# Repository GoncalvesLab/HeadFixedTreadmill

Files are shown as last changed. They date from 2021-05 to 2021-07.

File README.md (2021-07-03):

# HeadFixedTreadmill
This repository contains desgins to build a head-fixed linear treadmill apparatus and to run related data analysis.

Treadmill setups are a popular approach for in vivo recordings that require head-fixation and have been used by several labs
for example: Royer et al. 2012, Bittner et al. 2015, Danielson et al. 2016. This repository contains designs of custom-machined parts 
for a simple treadmill and head-fixation apparatus, as well as Arduino and Matlab code for tracking the position of the mouse and administer rewards.

Assembly:

Grounding of animal for lick detection: We implant a gold ground pin soldered to about 1 mm of tungsten wire above the cerebellum.
 
To assemble, clamp gold pin in a helping hand alligator clamp. Insert tungsten wire into the shallow hole of the flat end of the pin. Solder and then slip the wire approximately 1 mm from the pin. Likewise, solder a female connector to a long piece of wire (long enough to connect the mouse’s implanted pin to the lick counter) to ground the mouse. Solder a wire to the lick spout and connect it to the appropriate port on the lick counter. Licks will be sensed when a grounded mouse contacts the lick port, closing the circuit.

We tape the RFID scanner to the bottom of the mouse platform. Upload the RFID interface code to the Arduino Uno. Connect the RFID to the Arduino Uno, connect the following pins with jumper cables:

[RF522 Pin	->    Arduino Uno Pin (Digital)]

SDA	 ->         10

SCK	 ->         13

MOSI	->        11

MISO	->        12

IRQ	  ->        Not Used

GND	  ->        GND

RST	  ->        9

3.3 V	->        3.3V

To connect the Arduino Uno to the NI breakout box, solder jumper cables so that they have a split in one end. In other ones, one end of the cable will have a single tip (plugged into Arduino), and the other will have two tips (plugged into NI breakout box). This will give use two copies of the RFID signals: one is recorded and used for data analysis and the other is used as input to the pump. Connect the following pins with jumper cables:

[Arduino Uno Pin (Digital) ->	NI Breakout Box (Digital)]

2	-> P0-6 and PFI-5

3 -> P0-5 and PFI-4

4	-> P0-4 and PFI-3

5	-> P0-3 and PFI-2

6 -> P0-2 and PFI-1

Upload the rotary encoder interface code to the Arduino Due. To connect the rotary encoder to the Arduino Due, connect the following pins with jumper cables:

[Encoder Pins ->	Arduino Due Pins (Digital)]

Pin 1 (GND) ->	GND

Pin 2 	-> Not used

Pin 3 (Chan A) ->	3

Pin 4 (Vcc)	-> 5V

Pin 5 (Chan B) ->	4

To connect the Arduino Due to the NI breakout box, connect the DAC1 pin and a GND pin on the Due to a BNC adapter cable (DAC1 to voltage and GND to GND). Connect the BNC adapter to a BNC analog input on the NI breakout box (we use port analog input 0, or AI0).

To connect the lick counter to the breakout box, plug a BNC adapter cable into the lick counter output. Plus the voltage line into the port0/line7 on the NI breakout box and the GND into one of the digital GND ports.

For the pump command, we use a BNC splitter to send the output to the water pump for reward administration as well as to an input on the NI breakout box to record the command. To connect the NI breakout box to the water pump, plug a BNC adapter into digital port 0/line 0 and GND. Plug the adapter into a splitter. Use a BNC cable to plug one line into analog input 1 (AI1) and use a BNC adapter to plug the other line into the pump. For this, plug the voltage line into pin 2 on the pump's serial port and the GND into pin 9 of the pump's serial port.
 
Make sure jumper cables are stably connected. We happened to have old jumper cables whose pins fit perfectly into the pump TTL port, but many jumper cables fell out too easily to be used.

Acknowledgements:

The rotary encoder interface that tracks the velocity of the mouse is based on code by Steven Sawtelle (Janelia Research Campus).
The head-fixation bar was adapted from designs by the Golshani and Aharoni labs (UCLA).
The data acquisition routines in Matlab were adapted from code written by the Sjulson and Batista-Brito Labs (Einstein). We thank
Ehsan Sabri, Eliezyer Fermino De Oliveira, Luke Sjulson and Renata Batista-Brito for their technical advice and assistance.

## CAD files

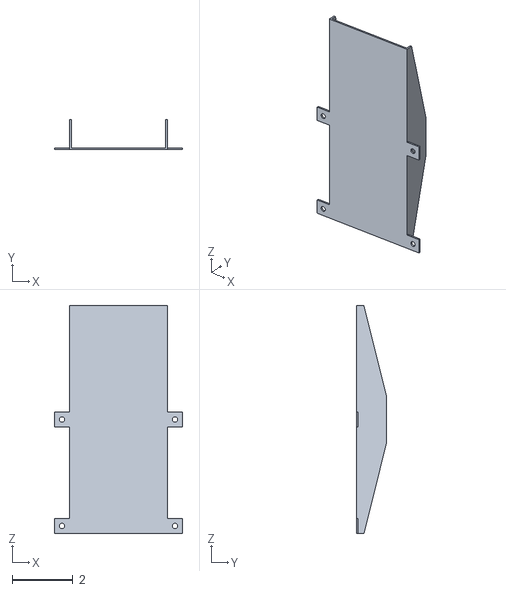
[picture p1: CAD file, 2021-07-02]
MousePlatform.stl
4.22 x 1.00 x 7.50

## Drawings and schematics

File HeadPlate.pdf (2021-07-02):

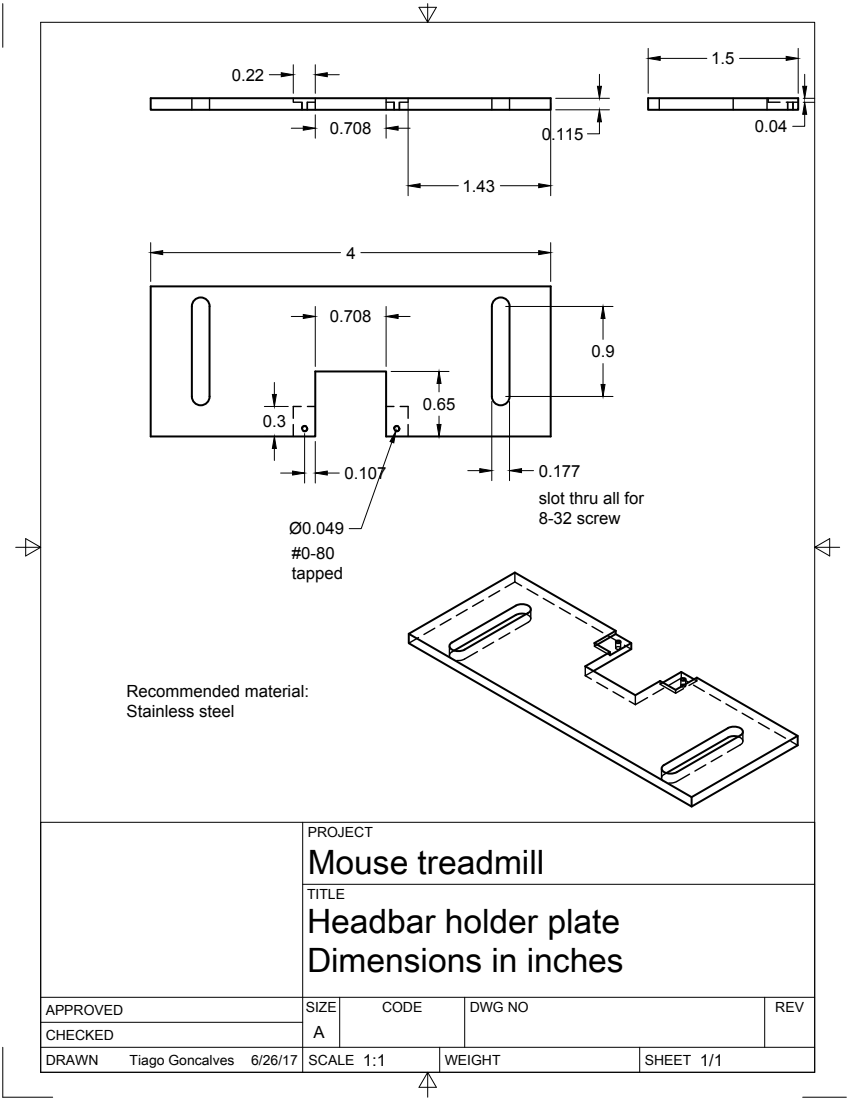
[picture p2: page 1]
SIZE; CODE; DWG NO; REV; Tiago Goncalves; Recommended material: Stainless steel

slot thru all for
8-32 screw

PROJECT
Mouse treadmill
Headbar holder plate
Dimensions in inches

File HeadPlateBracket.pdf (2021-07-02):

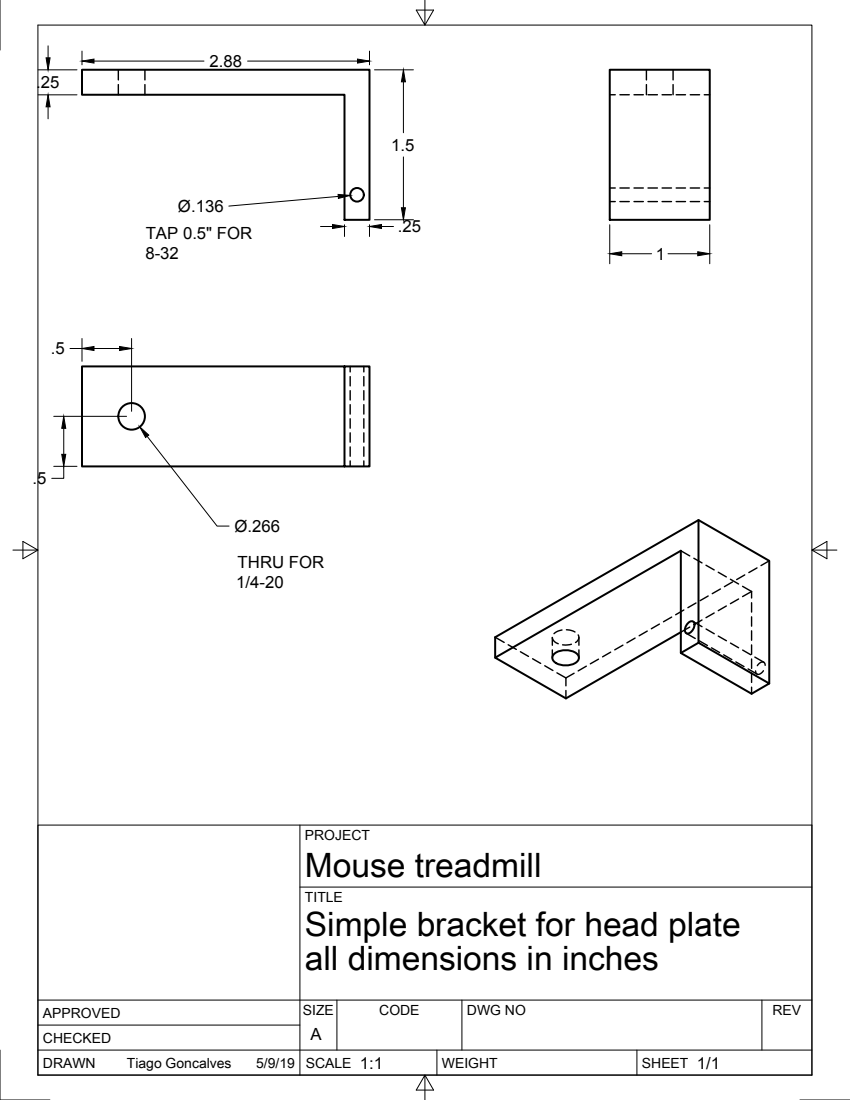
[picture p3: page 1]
SIZE; CODE; DWG NO; REV; Tiago Goncalves; TAP 0.5" FOR; THRU FOR

PROJECT
Mouse treadmill
Simple bracket for head plate
all dimensions in inches

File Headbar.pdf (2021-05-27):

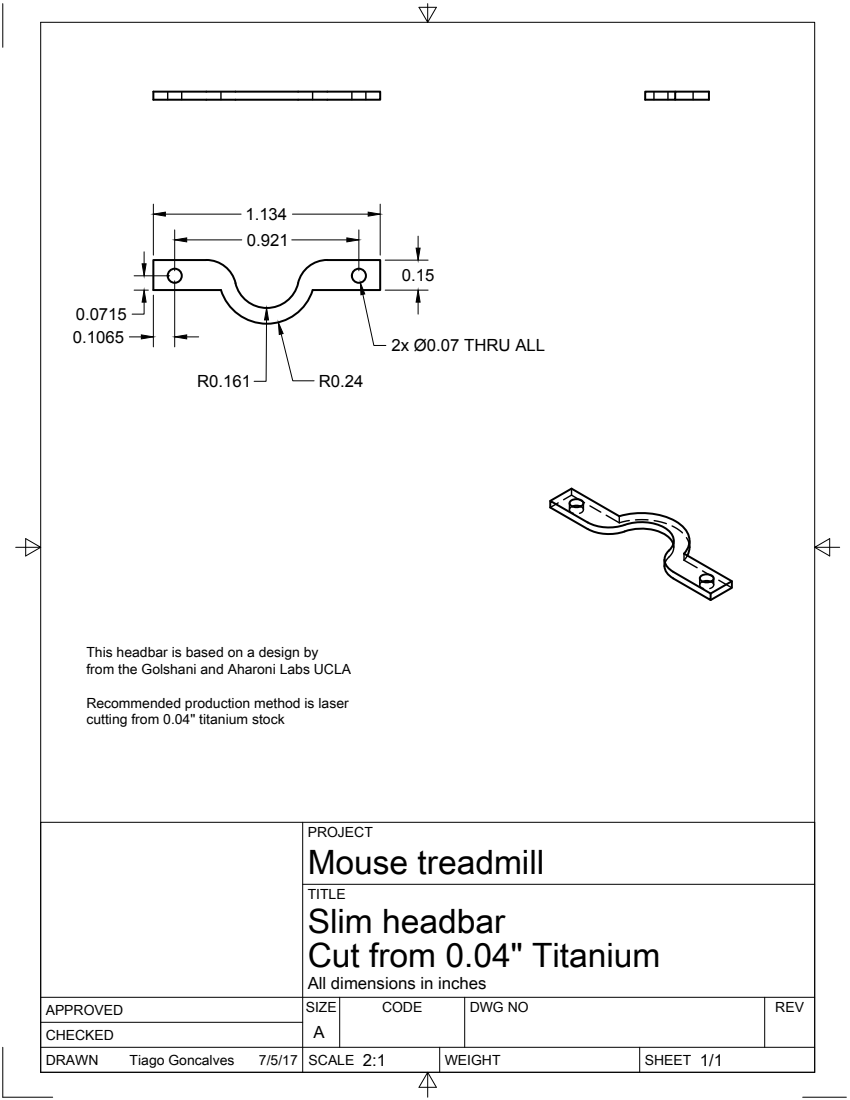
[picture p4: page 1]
SIZE; CODE; DWG NO; REV; Tiago Goncalves; 2x Ø0.07 THRU ALL

This headbar is based on a design by
from the Golshani and Aharoni Labs UCLA
Recommended production method is laser
cutting from 0.04" titanium stock

PROJECT
Mouse treadmill
Slim headbar
Cut from 0.04" Titanium

All dimensions in inches

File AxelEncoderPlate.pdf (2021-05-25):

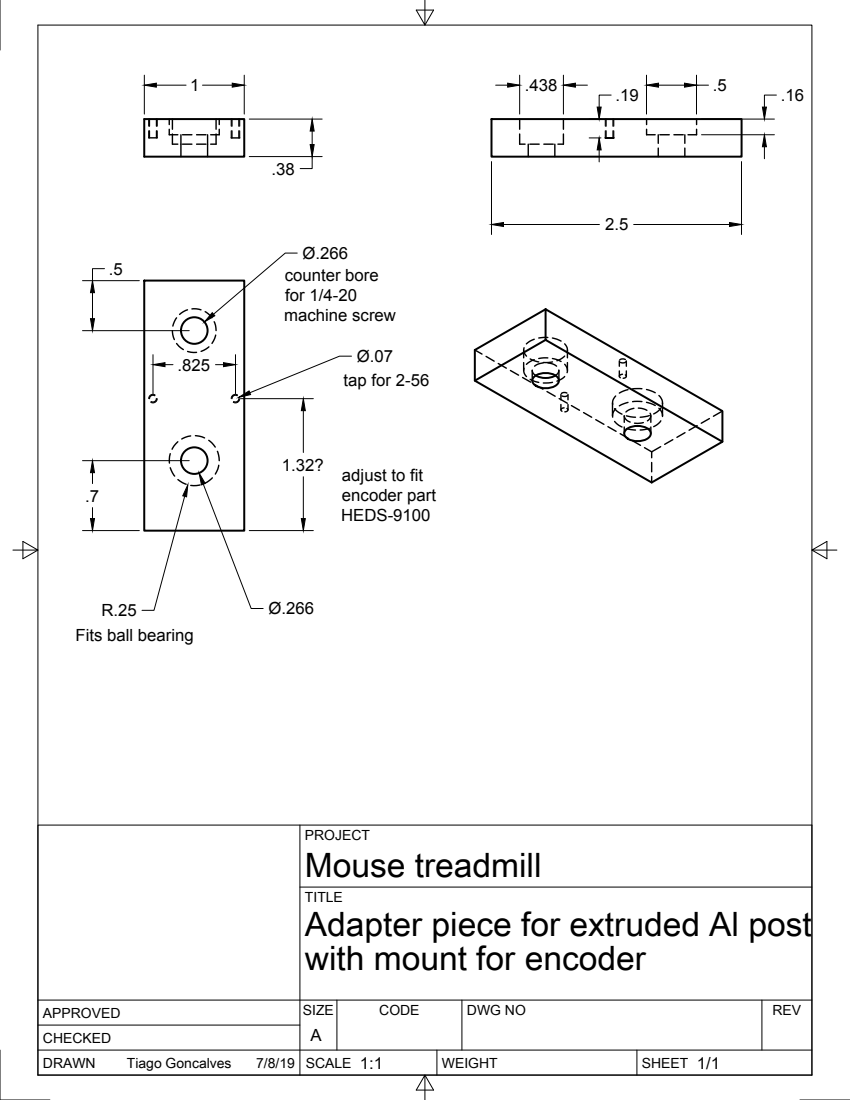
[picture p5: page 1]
SIZE; CODE; DWG NO; REV; Tiago Goncalves; counter bore for 1/4-20 machine screw; tap for 2-56

adjust to fit
encoder part
HEDS-9100

Fits ball bearing

PROJECT
Mouse treadmill
Adapter piece for extruded Al post
with mount for encoder

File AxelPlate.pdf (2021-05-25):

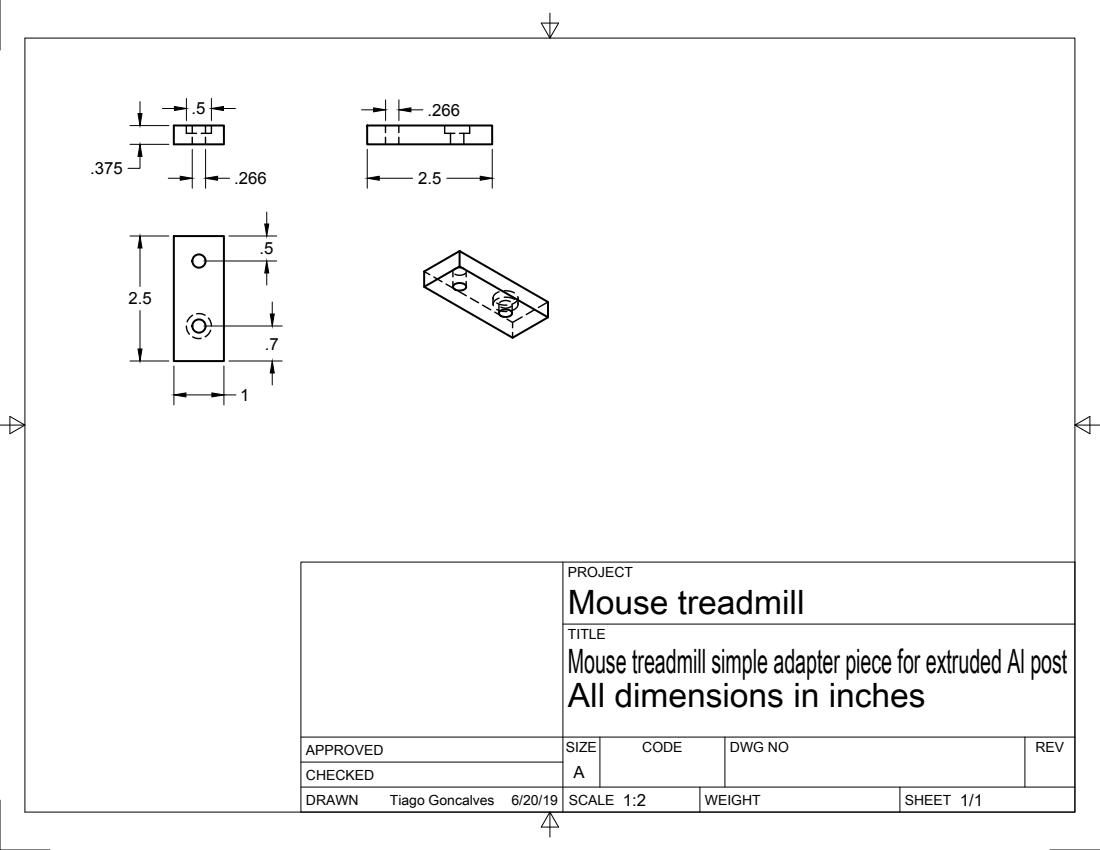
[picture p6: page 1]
SIZE; CODE; DWG NO; REV; Tiago Goncalves

PROJECT
Mouse treadmill
Mouse treadmill simple adapter piece for extruded Al post
All dimensions in inches

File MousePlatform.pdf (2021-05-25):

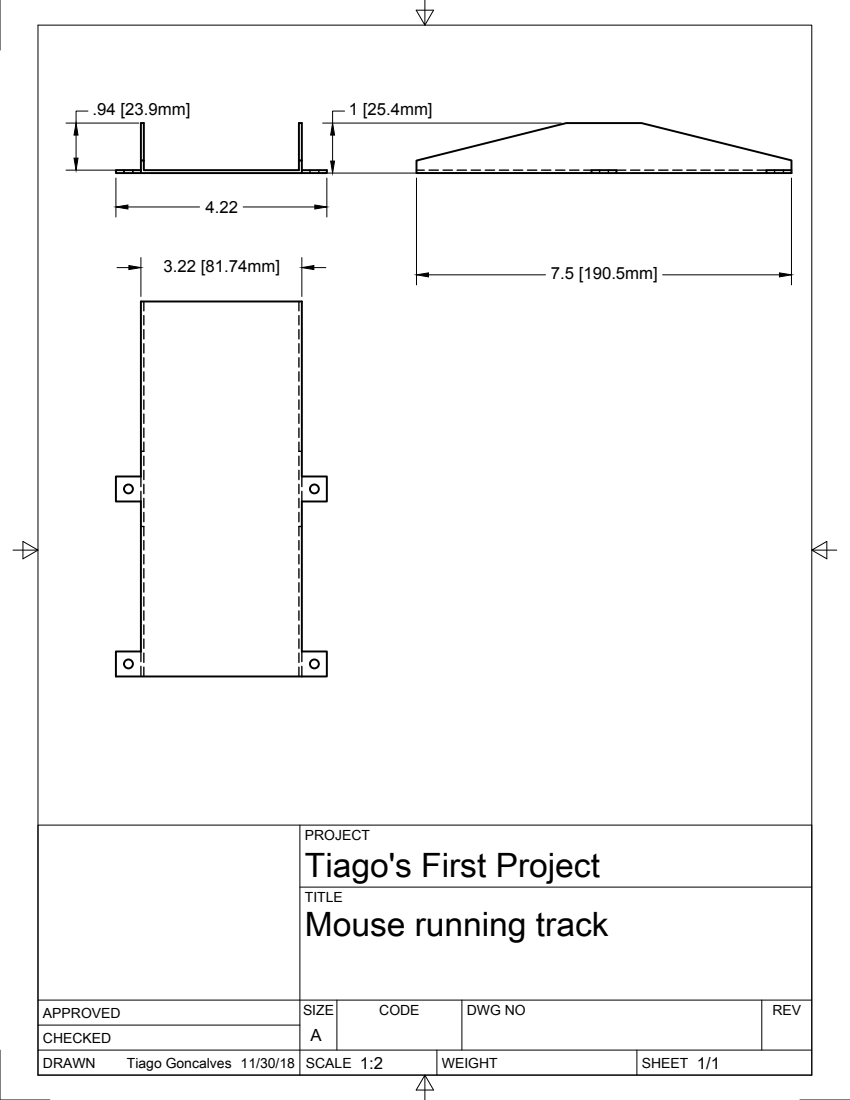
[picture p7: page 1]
SIZE; CODE; DWG NO; REV; Tiago Goncalves 11/30/18

PROJECT
Tiago's First Project
Mouse running track

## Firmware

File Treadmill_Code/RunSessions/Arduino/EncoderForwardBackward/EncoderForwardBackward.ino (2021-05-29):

// This code is based on the Janelia Encoder Interface for Mouse Treadmill
// by Steve Sawtelle (Janelia Research Campus)
// The original code can be obtained here: 
// https://www.janelia.org/open-science/encoder-interface-for-mouse-treadmill
// 
// The original file was modified so that it runs on Arduino Due and encodes both Backward and Forward motion
// Modified by Tiago Goncalves
// 
//
//EncoderInterfaceT3
//
//  Read the encoder and translate to a distance and send over USB-Serial and DAC
//  Teensy 3.2 Arduino 1.8.3 with Teensy Extensions
//
//  This designed to be easy to assemble. The cables are soldered directly to Teensy 3.2.
//  Encoder A - pin 3
//  Encoder B - pin 4
//  Encoder VCC - Vin
//  Encoder ground - GND
//  Analog Out - A1/DAC
//  Analog ground - AGND
//
// Steve Sawtelle
// jET
// Janelia
// HHMI 
//

#define VERSION "20180207 - modified by Goncalves Lab"
// ===== VERSIONS ======

#define MAXSPEED    1000.0f  // maximum speed for dac out (mm/sec)
#define MAXDACVOLTS 2.5f    // DAC ouput voltage at maximum speed
#define MAXDACCNTS 4095.0f // maximum dac value

float maxDACval = MAXDACVOLTS * MAXDACCNTS / 3.3; // limit dac output to max allowed

#define encAPin 3
#define encBPin 4
#define dacPin  DAC1
//#define idxPin  2  // not used here

// counts per rotation of treadmill encoder wheel
// 200 counts per rev
// 1.03" per rev
// so - 1.03 * 25.4 * pi / 200 /1000 = microns/cnt

#define MM_PER_COUNT 410950  // actually 1/10^6mm per count since we divide by usecs
#define DIST_PER_COUNT ((float)MM_PER_COUNT/1000000.0)
//(float)0.41095

#define SPEED_TIMEOUT 50000  // if we don't move in this many microseconds assume we are stopped

static float runSpeed = 0;
static float lastSpeed = 0;
volatile uint32_t lastUsecs;
volatile uint32_t thisUsecs;
volatile uint32_t encoderUsecs;
volatile float distance = 0;

#define FW 1
#define BW -1
int dir = FW;

// ------------------------------------------
// interrupt routine for ENCODER_A rising edge
// ---------------------------------------------
void encoderInt()
{   
  int ENCA = digitalRead(encAPin);  // always update output 
  int ENCB = digitalRead(encBPin); 
  if (ENCA == ENCB )    // figure out the direction  
  {   
 //   Serial.print('B');
    dir = BW;
    thisUsecs = micros();
    encoderUsecs = thisUsecs - lastUsecs;
    lastUsecs = thisUsecs;
    runSpeed = (float)MM_PER_COUNT / encoderUsecs;
    distance -= DIST_PER_COUNT;
  }  
  else
  {
 //   Serial.print('F');
    dir = FW;
    thisUsecs = micros();
    encoderUsecs = thisUsecs - lastUsecs;
    lastUsecs = thisUsecs;
    runSpeed = (float)MM_PER_COUNT / encoderUsecs;
    distance += DIST_PER_COUNT;
  }  
}


void setup()
{
  Serial.begin(19200);
  while( !Serial);   // if no serial USB is connected, may need to comment this out
  pinMode(encAPin, INPUT_PULLUP); // sets the digital pin as input
  pinMode(encBPin, INPUT_PULLUP); // sets the digital pin as input
  analogWriteResolution(12);

  Serial.print("Treadmill Interface V: ");
  Serial.println(VERSION);
  Serial.println("distance,speed");
  Serial.println(maxDACval);

  lastUsecs = micros();
  attachInterrupt(encAPin, encoderInt, RISING); // check encoder every A pin rising edge
}

void loop() 
{ 
  noInterrupts();
  uint32_t now = micros();
  uint32_t lastU = lastUsecs;
  if( (now > lastU) && ((now - lastU) > SPEED_TIMEOUT)  )
  {   // now should never be < lastUsecs, but sometiems it is
      // I question if noInterupts works
     runSpeed = 0;
  }        
  interrupts(); 

  if( runSpeed != lastSpeed && dir == FW )
  {   
      lastSpeed = runSpeed;
      float dacval = (maxDACval/2) + (runSpeed/MAXSPEED * maxDACval/2);  
      if( dacval < 0 ) dacval = maxDACval/2;
      if( dacval > maxDACval) dacval = maxDACval;
      
      Serial.print(distance);
      Serial.print(",");
      Serial.println(dacval);    
      analogWrite(dacPin, dacval);
  }
  if(runSpeed != lastSpeed && dir == BW)
  {
      lastSpeed = runSpeed;
      float dacval = (maxDACval/2) - ((runSpeed/MAXSPEED) * (maxDACval/2)); 
      if( dacval < 0 ) dacval = maxDACval/2;
      if( dacval > maxDACval) dacval = 0;
      
      Serial.print(distance);
      Serial.print(",");
      Serial.println(dacval);    
      analogWrite(dacPin, dacval);
  }

}

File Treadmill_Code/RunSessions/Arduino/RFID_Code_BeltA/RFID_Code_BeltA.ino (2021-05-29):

// This code is based on the examples included in MFRC522 library
// Modify to include the UIDs of the tags on your treadmill belt

#include<SPI.h>
#include<MFRC522.h>

//creating mfrc522 instance
#define RSTPIN 9
#define SSPIN 10
MFRC522 rc(SSPIN, RSTPIN);

int readsuccess;

/* the following are the UIDs of the card which are authorised
    to know the UID of your card/tag use the example code 'DumpInfo'
    from the library mfrc522 it give the UID of the card as well as 
    other information in the card on the serial monitor of the arduino*/

    //byte defcard[4]={0x32,0xD7,0x0F,0x2B}; // if you only want one card
byte defcard[][4]={{0xC4,0x11,0xCB,0xCF},{0xF4,0x2B,0xC9,0xCF},{0xE4,0x2B,0xC9,0xCF},{0xD4,0x2B,0xC9,0xCF},{0xC4,0x2B,0xC9,0xCF}}; //for multiple cards
//byte defcard[][4]={{0xC4,0x11,0xCB,0xCF},{0xF4,0x2B,0xC9,0xCF},{0xE4,0x2B,0xC9,0xCF},{0xD4,0x2B,0xC9,0xCF},{0xD4,0x19,0xC7,0xCF}}; //for reversal learning; ID of reward tag changed
int N=5; //change this to the number of cards/tags you will use
byte readcard[4]; //stores the UID of current tag which is read

void setup() {
//Serial.begin(9600); //for debugging purposes

SPI.begin();
rc.PCD_Init(); //initialize the receiver  
rc.PCD_DumpVersionToSerial(); //show details of card reader module

pinMode(6,OUTPUT); //Zone 1 digital output, match = 0, channel 6
pinMode(5,OUTPUT); //Zone 2 digital output, match = 1, channel 5
pinMode(4,OUTPUT); //Zone 3 digital output, match = 2, channel 4
pinMode(3,OUTPUT); //Zone 4 digital output, match = 3, channel 3
pinMode(2,OUTPUT); //Reward digital output, match = 4, channel 2

//if tag unrecognized match = 5


//Serial.println(F("Recognized RFID tags are")); //display authorised cards just to demonstrate you may comment this section out
//for(int i=0;i<N;i++){ 
//  Serial.print(i+1); for debugging purposes
//  Serial.print("  ");
//    for(int j=0;j<4;j++){
//      Serial.print(defcard[i][j],HEX);
//      }
//      Serial.println("");
//     }
//Serial.println("");
//
//Serial.println(F("Scanning for RFID tags..."));
}


void loop() {
  
readsuccess = getid();

if(readsuccess){
 
  int match=5;

//this is the part where compare the current tag with pre defined tags
  for(int i=0;i<N;i++){
    //Serial.print("Testing Against Authorised card no: ");
    //Serial.println(i+1);
    if(!memcmp(readcard,defcard[i],4)){
      match=i;
      }
    
  }
    
  
   if(match==0)
      {//Serial.println("Recognized tag detected: Zone 1");
        digitalWrite(6,HIGH);
        delay(500);
        digitalWrite(6,LOW);
        delay(300);   
      }

    if(match==1)
      {//Serial.println("Recognized tag detected: Zone 2");
        digitalWrite(5,HIGH);
        delay(500);
        digitalWrite(5,LOW);
        delay(300);  
      }

    if(match==2)
      {//Serial.println("Recognized tag detected: Zone 3");
        digitalWrite(4,HIGH);
        delay(500);
        digitalWrite(4,LOW);
        delay(300);  
      } 

     if(match==3)
      {//Serial.println("Recognized tag detected: Zone 4");
        digitalWrite(3,HIGH);
        delay(500);
        digitalWrite(3,LOW);
        delay(300);  
      } 

     if(match==4)
      {//Serial.println("Recognized tag detected: Reward");
        digitalWrite(2,HIGH);
        delay(500);
        digitalWrite(2,LOW);
        delay(300);  
      } 
      
     //if(match==5) {
      //Serial.println("Unrecognized tag detected");
      //}
  
  }
}
//function to get the UID of the card
int getid(){  
  if(!rc.PICC_IsNewCardPresent()){
    return 0;
  }
  if(!rc.PICC_ReadCardSerial()){
    return 0;
  }
 
  
  //Serial.println("THE UID OF THE SCANNED TAG IS:");
  
  for(int i=0;i<4;i++){
    readcard[i]=rc.uid.uidByte[i]; //storing the UID of the tag in readcard
    //Serial.print(readcard[i],HEX);
    
  }
   //Serial.println("");
   //Serial.println("Now Comparing with Authorised cards");
  rc.PICC_HaltA();
  
  return 1;
}
